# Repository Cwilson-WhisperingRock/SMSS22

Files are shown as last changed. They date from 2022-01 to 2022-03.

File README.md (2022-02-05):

SMSS22 : Smart Motor Syringe System
Winter 2022
Connor Wilson 

This repository is the lastest installment for the Smart Motor Syringe System.

~ Hub.py is the Hub controller file (raspberry Pi) that controls the three arduino motor controllers
	- The arduino motor controllers use Motor_controller.ino
		> Motor_controller.ino can be toggled to operate with the Hub.py using the #define I2C_COMMS
			or serial comms through the arduino IDE #define SERIAL_comms
			
~ Curses_Practice is a folder for getting familiar with the curses terminal GUI 

~ I2C_Practice is a folder for becoming familiar with I2C comms between the raspberry Pi's SMBus and arduino Wire libraries

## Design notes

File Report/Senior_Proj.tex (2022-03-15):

\documentclass[journal]{IEEEtran}
%
% If IEEEtran.cls has not been installed into the LaTeX system files,
% manually specify the path to it like:
% \documentclass[journal]{../sty/IEEEtran}

% *** CITATION PACKAGES ***
%
\usepackage[sorting =none]{biblatex}
\addbibresource{Citations.bib}

\usepackage{caption}
\usepackage{makecell}
\usepackage{fourier}
\usepackage{float}
\usepackage{color,soul}    
\usepackage{amssymb}

\usepackage{listings}
\usepackage{xcolor}

%New colors defined below
\definecolor{codegreen}{rgb}{0,0.6,0}
\definecolor{codegray}{rgb}{0.5,0.5,0.5}
\definecolor{codepurple}{rgb}{0.58,0,0.82}
\definecolor{backcolour}{rgb}{0.95,0.95,0.92}
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
  % declare the path(s) where your graphic files are
  % \graphicspath{{../pdf/}{../jpeg/}}
  % and their extensions so you won't have to specify these with
  % every instance of \includegraphics
  % \DeclareGraphicsExtensions{.pdf,.jpeg,.png}
\else
  % or other class option (dvipsone, dvipdf, if not using dvips). graphicx
  % will default to the driver specified in the system graphics.cfg if no
  % driver is specified.
  % \usepackage[dvips]{graphicx}
  % declare the path(s) where your graphic files are
  % \graphicspath{{../eps/}}
  % and their extensions so you won't have to specify these with
  % every instance of \includegraphics
  % \DeclareGraphicsExtensions{.eps}
\fi
% graphicx was written by David Carlisle and Sebastian Rahtz. It is
% required if you want graphics, photos, etc. graphicx.sty is already
% installed on most LaTeX systems. The latest version and documentation
% can be obtained at: 
% http://www.ctan.org/pkg/graphicx
% Another good source of documentation is "Using Imported Graphics in
% LaTeX2e" by Keith Reckdahl which can be found at:
% http://www.ctan.org/pkg/epslatex
%
% latex, and pdflatex in dvi mode, support graphics in encapsulated
% postscript (.eps) format. pdflatex in pdf mode supports graphics
% in .pdf, .jpeg, .png and .mps (metapost) formats. Users should ensure
% that all non-photo figures use a vector format (.eps, .pdf, .mps) and
% not a bitmapped formats (.jpeg, .png). The IEEE frowns on bitmapped formats
% which can result in "jaggedy"/blurry rendering of lines and letters as
% well as large increases in file sizes.
%
% You can find documentation about the pdfTeX application at:
% http://www.tug.org/applications/pdftex

% *** MATH PACKAGES ***
%
\usepackage{amsmath}
% A popular package from the American Mathematical Society that provides
% many useful and powerful commands for dealing with mathematics.
%
% Note that the amsmath package sets \interdisplaylinepenalty to 10000
% thus preventing page breaks from occurring within multiline equations. Use:
\interdisplaylinepenalty=2500
% after loading amsmath to restore such page breaks as IEEEtran.cls normally
% does. amsmath.sty is already installed on most LaTeX systems. The latest
% version and documentation can be obtained at:
% http://www.ctan.org/pkg/amsmath

% *** SPECIALIZED LIST PACKAGES ***
%
\usepackage{algorithmic}
% algorithmic.sty was written by Peter Williams and Rogerio Brito.
% This package provides an algorithmic environment fo describing algorithms.
% You can use the algorithmic environment in-text or within a figure
% environment to provide for a floating algorithm. Do NOT use the algorithm
% floating environment provided by algorithm.sty (by the same authors) or
% algorithm2e.sty (by Christophe Fiorio) as the IEEE does not use dedicated
% algorithm float types and packages that provide these will not provide
% correct IEEE style captions. The latest version and documentation of
% algorithmic.sty can be obtained at:
% http://www.ctan.org/pkg/algorithms
% Also of interest may be the (relatively newer and more customizable)
% algorithmicx.sty package by Szasz Janos:
% http://www.ctan.org/pkg/algorithmicx

% *** ALIGNMENT PACKAGES ***
%
\usepackage{array}
% Frank Mittelbach's and David Carlisle's array.sty patches and improves
% the standard LaTeX2e array and tabular environments to provide better
% appearance and additional user controls. As the default LaTeX2e table
% generation code is lacking to the point of almost being broken with
% respect to the quality of the end results, all users are strongly
% advised to use an enhanced (at the very least that provided by array.sty)
% set of table tools. array.sty is already installed on most systems. The
% latest version and documentation can be obtained at:
% http://www.ctan.org/pkg/array

% IEEEtran contains the IEEEeqnarray family of commands that can be used to
% generate multiline equations as well as matrices, tables, etc., of high
% quality.

\begin{document}
\graphicspath{ {./Images/} }
%
% paper title
% Titles are generally capitalized except for words such as a, an, and, as,
% at, but, by, for, in, nor, of, on, or, the, to and up, which are usually
% not capitalized unless they are the first or last word of the title.
% Linebreaks \\ can be used within to get better formatting as desired.
% Do not put math or special symbols in the title.
\title{Smart Motor Syringe System}
%
%
% author names and IEEE memberships
% note positions of commas and nonbreaking spaces ( ~ ) LaTeX will not break
% a structure at a ~ so this keeps an author's name from being broken across
% two lines.
% use \thanks{} to gain access to the first footnote area
% a separate \thanks must be used for each paragraph as LaTeX2e's \thanks
% was not built to handle multiple paragraphs
%

\author{Connor~Wilson,~\IEEEmembership{Member,~IEEE,} \\
        \small{EE Dept. Senior Project, \emph{California Polytechnic San Luis Obispo}, Winter 2022\\
        Advisor: Dr. Benjamin G. Hawkins}
        %John~Doe,~\IEEEmembership{Fellow,~OSA,}
        %and~Jane~Doe,~\IEEEmembership{Life~Fellow,~IEEE}% <-this % stops a space
%\thanks{B. Hawkins was with the Department
%of Electrical and Biomedical Engineering, California Polytechnic San Luis Obispo,
%CA, 93405 }% <-this % stops a space
%\thanks{Conrad Chan is with California Polytechnic San Luis Obispo}% <-this % stops a space
%\thanks{Manuscript received April 19, 2005; revised August 26, 2015.}}
}

% note the % following the last \IEEEmembership and also \thanks - 
% these prevent an unwanted space from occurring between the last author name
% and the end of the author line. i.e., if you had this:
% 
% \author{....lastname \thanks{...} \thanks{...} }
%                     ^------------^------------^----Do not want these spaces!
%
% a space would be appended to the last name and could cause every name on that
% line to be shifted left slightly. This is one of those "LaTeX things". For
% instance, "\textbf{A} \textbf{B}" will typeset as "A B" not "AB". To get
% "AB" then you have to do: "\textbf{A}\textbf{B}"
% \thanks is no different in this regard, so shield the last } of each \thanks
% that ends a line with a % and do not let a space in before the next \thanks.
% Spaces after \IEEEmembership other than the last one are OK (and needed) as
% you are supposed to have spaces between the names. For what it is worth,
% this is a minor point as most people would not even notice if the said evil
% space somehow managed to creep in.

% The paper headers
%\markboth{Journal of \LaTeX\ Class Files,~Vol.~14, No.~8, August~2015}%
%{Shell \MakeLowercase{\textit{et al.}}: Bare Demo of IEEEtran.cls for IEEE Journals}
% The only time the second header will appear is for the odd numbered pages
% after the title page when using the twoside option.
% 
% *** Note that you probably will NOT want to include the author's ***
% *** name in the headers of peer review papers.                   ***
% You can use \ifCLASSOPTIONpeerreview for conditional compilation here if
% you desire.

% If you want to put a publisher's ID mark on the page you can do it like
% this:
%\IEEEpubid{0000--0000/00\$00.00~\copyright~2015 IEEE}
% Remember, if you use this you must call \IEEEpubidadjcol in the second
% column for its text to clear the IEEEpubid mark.

% use for special paper notices
%\IEEEspecialpapernotice{(Invited Paper)}

% make the title area
\maketitle

% As a general rule, do not put math, special symbols or citations
% in the abstract or keywords.
\begin{abstract}
In this document a proof-of-concept design is developed and implementation to showcase the latest development in an ongoing effort to produce a series of automated syringe pumps.
\end{abstract}

% Note that keywords are not normally used for peerreview papers.
%\begin{IEEEkeywords}
%IEEE, IEEEtran, journal, \LaTeX, paper, template.
%\end{IEEEkeywords}

% For peer review papers, you can put extra information on the cover
% page as needed:
% \ifCLASSOPTIONpeerreview
% \begin{center} \bfseries EDICS Category: 3-BBND \end{center}
% \fi
%
% For peerreview papers, this IEEEtran command inserts a page break and
% creates the second title. It will be ignored for other modes.
\IEEEpeerreviewmaketitle

\section{Introduction}
    \IEEEPARstart{T}{here} is a desire to control flow rates in syringes in a steady and automated manner in the medical field; whether that be IV fluids or micro-fluids. According to PR NewsWire, the automated syringe pump market is currently valued at \$4 billion USD and is set to double its growth by 2030 \cite{cision}. These numbers suggest administering fluids in a controlled manner is a profitable and valuable piece of technology.
    
    However, this task is difficult to do manually, requiring precise digital control to achieve success. Because this device is related to medical and bio-engineering research, greater emphasis is placed on maintaining consistent flow rates and precision control. To achieve this key feature, typical syringe pumps utilize the precision of micro-controllers, large stepper motors, and reduction gear ratios in the drive train.
    
    With the introduction of precision control, keeping this project low cost is a secondary goal to make medical grade technology readily available. While existing products in the market are numerous, they are traditionally priced above \$1000 USD and are not easily programmable nor user friendly. Using readily available, non-proprietary hardware and software, I aim to provide reliable automated syringe systems for a fraction of the cost. This system of syringe pumps will also be controlled from a single controller, allowing the user to operate without manually addressing individual devices. This hub controller will add hierarchy that provides a more native and intuitive interface for the user, saving time and other resources used during setup.
    
    %Not sure if I should leave this part in or not??!
    It should be noted that my contribution to this project does not constitute a finished product but rather an ongoing pursuit for the minimum viable product as defined by Doctor Ben Hawkins.

\section{Background}

    \subsection{Purpose of a Syringe Pump}
        A syringe pump (or driver) is defined as a “small infusion pump, used to gradually
        administer small amounts of fluid (with or without medication) to a patient or for use in chemical and biomedical research.” \cite{wiki-pump} The need for slow incorporation of fluids is used in many applications. Intravenous (IV) therapies, for example, require syringe pumps in order to deliver medication over the course of several minutes or hours. Automating these doses removes most human error in high-risk procedures while saving the medical staff man-hours.
        
        \begin{figure}[H]
            \centering
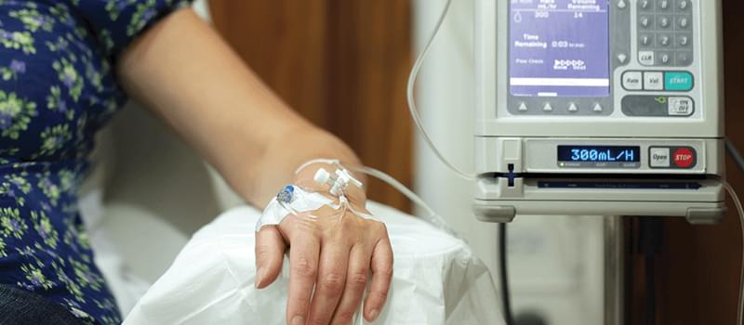
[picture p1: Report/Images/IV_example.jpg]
            
            \caption{Example of a Syringe Pump's IV Application \cite{howto-syringe}}
            \label{fig:IV_example}
        \end{figure}
        
        Additional uses for syringe pumps lie in micro-fluid research applications such as: enzyme kinetics, chemical synthesis, and potentially dangerous chemical reactions. For this project, the immediate use of this product will be for Dr. Ben Hawkins's research in enzyme solution gradients.
        
        \begin{figure}[H]
            \centering
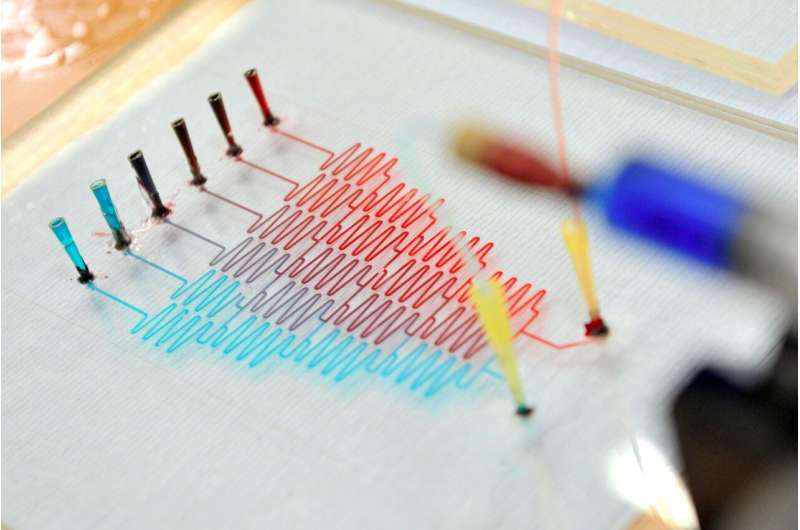
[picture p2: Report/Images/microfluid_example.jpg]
            
            \caption{Example of Microfluid Application \cite{mf_ex}}
            \label{fig:mf_example}
        \end{figure}
        
    \subsection{Description of the Smart Motor Syringe Pump}
    
        The SMSS (Smart Motor Syringe Pump) performs as the defined syringe pump, including but not limited to: output accurate/precise flow rates, display input/output hardware parameters, and control several syringe pumps, all while remaining under \$500 USD.
        
        The SMSS also aims to solve two problems, the first being inconsistent flow rates. Looking at existing technology, most low end pumps work on the basis of summing impulses over time such as the NE-300 in Figure \ref{fig:baddata_example}. An ideal pump would have smooth flow and quick transient responses. However, the main concern for the SMSS in this stage is to maintain a smooth flow rate and address sluggish response times in another prototype. Quintessentially, the SMSS is built to output flow rates that are precise and accurate. An understanding of the system’s plant and controller interface is required to operate within the desired tolerances and well worth the time investment. This will be discussed later in the paper.
        
         \begin{figure}[H]
            \centering
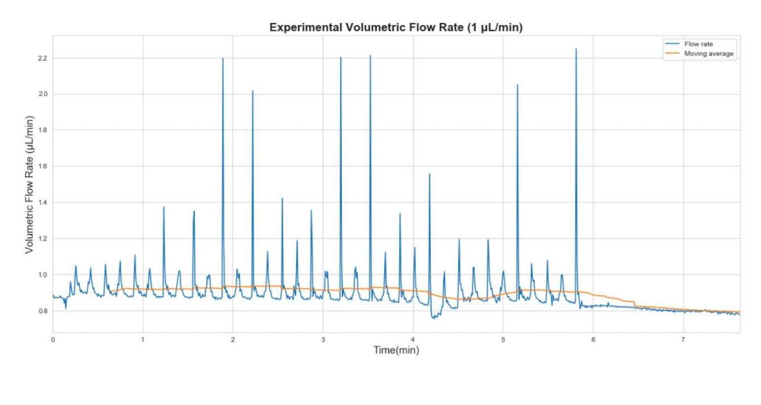
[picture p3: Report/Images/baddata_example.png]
            
            \caption{Output Flow from a NE-300 Syringe Pump \cite{conrads}}
            \label{fig:baddata_example}
        \end{figure}
        
        The second problem arises with the addition of other syringe pumps: multiple pumps will often require a synchronized start/stop time from which to collect data from. The main/sub hierarchy implemented aims to synchronize the start/stop of several units and eliminate the errors presented when triggering each pump manually. 
        
        Looking broadly at this project, the SMSS aligns with a research market: laboratory applications that deliver small amounts of fluid while collecting data on the system. It should be noted that while syringe pumps can differ in applications, their internal structure is the same: they all consist of a stepper motor, pusher block, and a syringe holder (Figure \ref{fig:Pump_example}). 
        
        \begin{figure}[H]
            \centering
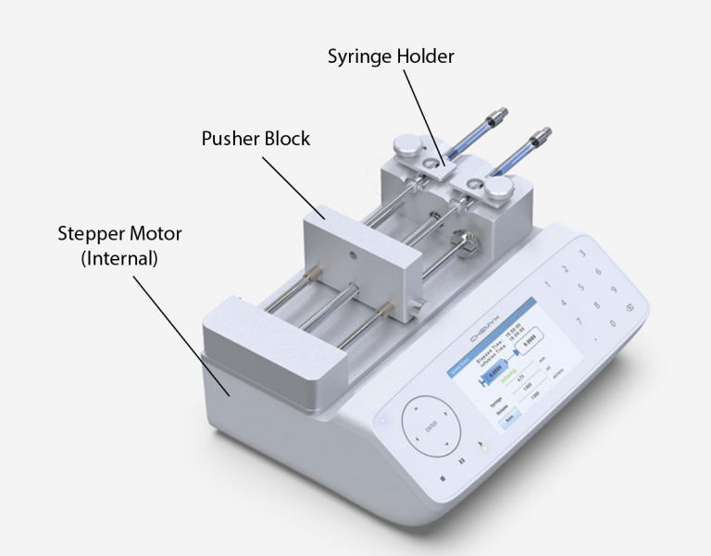
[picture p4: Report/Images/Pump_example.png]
            
            \caption{Components of a Syringe Pump \cite{example-syringe}}
            \label{fig:Pump_example}
        \end{figure}

        The SMSS makes use of the Raspberry Pi 3's computing power by implementing a display for the user; a feature forgotten on some devices on the market. The user interface prompts for user requests but also informs the user of resulting error codes, run time, and hardware issues with their requests.

\section{Product Planning and Research} 
    Evaluation of the SMSS and it's viability as a product requires an analysis of existing technology on the market. Only when I looked at the existing products could I determine the engineering requirements and priority of each.
    
    \subsection{Marketing}
        This subsection is focused on the marketing aspect of a syringe pump in an attempt to translate customer needs into a viable and cost effective product.
        
        \subsubsection{Marketing Research}
            Using Google's tool for search trends, there was a low number of searches in the US and internationally for syringe pumps. This signals that the amount of new customers looking to purchase an SMSS is small, or that existing customers in the market do not use Google to search for new products. These customers might look to a medical supplier or academic group when looking for a new syringe pump. The Dublin PRNewswire \cite{cision} has stated that the IV pump market is valued at \$4 billion USD (in 2020) and is expected to double by 2030. This speculation is pre-COVID but it does hold some merit. Looking at Figure \ref{fig:intern_interest}, there appears to be a larger customer base outside the US; range for Figure \ref{fig:intern_interest} is $\in$ (12-211) hits in January 2021.
            
            \begin{figure}[H]
                \centering
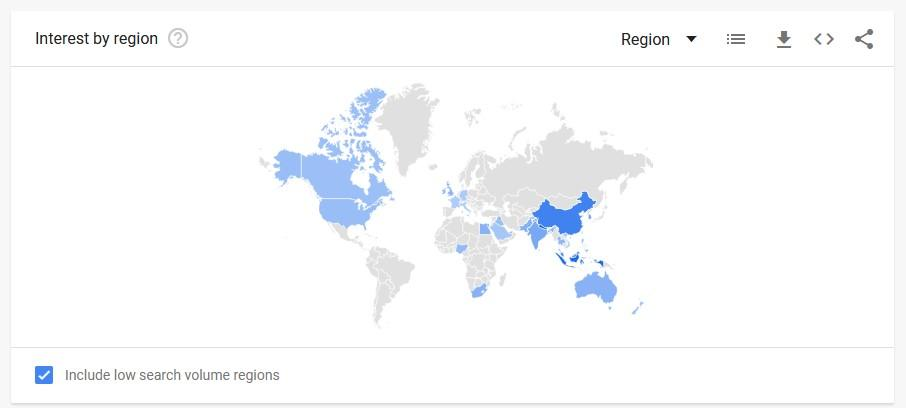
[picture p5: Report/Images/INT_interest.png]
                
                \caption{Global Google Search of "Syringe Pump" 2021 \cite{goog_trend}}
                \label{fig:intern_interest}
            \end{figure}
        
            Further information was gathered in Figure \ref{fig:search_option} when searching for syringe pumps: there are many applications and characteristics for existing products on the market. My sole customer's [Dr. Hawkins] request for a research-oriented device represents smaller portion when compared to infusions, but it should be noted that the SMSS can achieve the minimum viable product for multiple applications. Qualifying for various FDA medical device classes will be left up to the next iteration of the SMSS.
            
            \begin{figure}[H]
                \centering
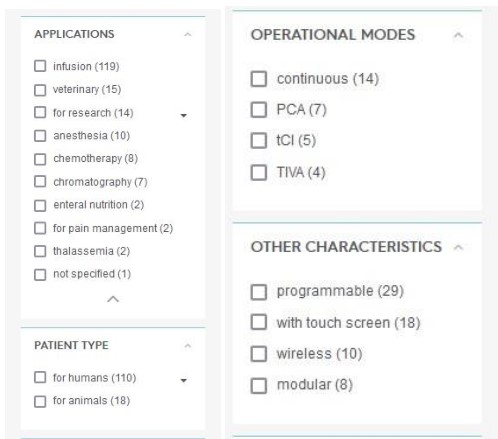
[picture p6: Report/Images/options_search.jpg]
                
                \caption{Options for Pumps in MedicalExpo.com \cite{goog_device}}
                \label{fig:search_option}
            \end{figure}

        \subsubsection{Customer Archetype}
            The Smart Motor Syringe System has many established competitors in the market but none have a portion over 40\%. All of these competitors have costly devices nearing \$5000 USD but come with features such as failure alarms, custom fluid capacity syringes, unique flow patterns, and battery backup power. However, after viewing a handful of device data sheets on MedicalExpo.com \cite{goog_device}, very few competitors provide testing data or flow rate tolerances. With our main customer being research oriented, the sensitivity of the pump's output is important. I believe bolstering and advertising the engineering requirements on top of the SMSS's steady output as the minimum viable product will carve out a spot in the syringe pump market.
            
            The table below provides three examples of the customer base.
            
            \begin{table}[H]
                \renewcommand{\arraystretch}{1.3}
                \caption{Customer Archetype}
                \label{table:CustArch}
                \begin{center}
                    \begin{tabular}{|c|c|c|c|}
                        \hline
                        \bfseries Customer&
                        \bfseries Description&
                        \bfseries Reason&
                        \bfseries Product Use\\
                        \hline
                        
                        \makecell[l]{Research\\Student}&
                        \makecell[l]{This group is \\
                                     likely to ad-\\
                                     opt new tech-\\
                                     nologies with\\
                                     an emphasis on\\
                                     easy-use DIY\\
                                     and low cost.}&
                        \makecell[l]{This group aims\\
                                     to utilize the\\
                                     minimum viable\\
                                     product aspect\\
                                     while remain-\\
                                     ing open to \\
                                     learning exper-\\
                                     iences around\\
                                     DIY and emerg-\\
                                     ing tech. The\\
                                     ability to buy\\ 
                                     multiple units\\
                                     and sync them\\
                                     is important\\
                                     for testing \\
                                     data.}&
                        \makecell[l]{This group will\\
                                     utilize this pr-\\
                                     oduct frequently\\
                                     but not in a \\
                                     commercial set-\\
                                     ting. I can exp-\\
                                     ect his product\\
                                     to remain rele-\\
                                     vant for a long\\
                                     period until re-\\
                                     placement over\\
                                     the course of \\
                                     a decade.}\\
                        \hline
                        
                        \makecell[l]{Remote\\Medical\\Worker}&
                        \makecell[l]{These customers\\
                                     are looking for\\
                                     a robust solut-\\
                                     ion that can be\\
                                     torn open and \\
                                     repaired. Cost\\
                                     is likely to be\\
                                     a factor.}&
                        \makecell[l]{Practicing medi-\\
                                     cine in remote\\
                                     locations means\\
                                     that supplies \\
                                     are limited. The\\
                                     need for medical\\
                                     attention will\\
                                     still require med-\\
                                     ical equipment.}&
                        \makecell[l]{This group will\\
                                     likely run the\\
                                     equipment into\\
                                     the ground and\\
                                     replace parts \\
                                     themselves. Cost\\
                                     is a strong fact-\\
                                     or as well as \\
                                     robustness and\\
                                     open-source \\
                                     likeness}\\
                        \hline
                        
                        \makecell[l]{Third-\\World\\Medical\\Center}&
                        \makecell[l]{These customers\\
                                     care most about\\
                                     the cost of the\\
                                     product as well\\
                                     as the function-\\
                                     ality. MVP and \\
                                     functionality \\
                                     are critical}&
                        \makecell[l]{Currency may \\
                                     not be equal \\
                                     to USD and req-\\
                                     uire a large \\
                                     portion of the\\
                                     budget to buy \\
                                     basic medical \\
                                     equipment.}&
                        \makecell[l]{[Same as above]}\\
                        \hline
        
                    \end{tabular}
                \end{center}
            \end{table}
            
            The following table outlines competitors in the market. It should be noted that most companies are overseas and have a large pool of products related to the medical field. This list is not shy of catheters, IV fluids, syringes, thermal components, 3-D imaging machines, and other augmented devices. One example is Norgren, a large Switzerland company. They have an international presence here in the US that shouldn't be excluded when researching domestic markets in the US. I should mention that it is not easy to track companies as a whole entity, but rather its branches and partners. Wellead is an example of a company here in the US that is difficult to contact or buy from locally. I believe a portion of these companies have third parties to sell and establish their branding within the medical market.
            
            The table below provides four examples of competing companies.
            
            \begin{table}[H]
                \renewcommand{\arraystretch}{1.3}
                \caption{Market Competitors}
                \label{table:Mark_compet}
                \begin{center}
                    \begin{tabular}{|c|c|}
                        \hline
                        \bfseries Market Leader&
                        \bfseries Description\\
                        \hline

                        
                        \cite{goog_device}&
                        \makecell[l]{Specializes in\\
                                     veterinary medical\\
                                     devices (Located\\
                                     in China)}\\
                        \hline
                        
                        
                        \cite{goog_device}&
                        \makecell[l]{Specialized in\\
                                     a wide variety \\
                                     of syringe pumps\\
                                     and medical equip-\\
                                     ment. One of the \\
                                     top 10 medical \\
                                     companies in this\\
                                     field. (Located in\\
                                     USA)}\\
                        \hline
                        
                        
                        \cite{goog_device}&
                        \makecell[l]{A small company \\
                                     with a good prod-\\
                                     uct line. (Located\\
                                     in China)}\\
                        \hline
                        
                        
                        \cite{goog_device}&
                        \makecell[l]{A pipetting comp-\\
                                     any that makes \\
                                     channel pumps and\\
                                     syringe pumps. \\
                                     (Located in Swit-\\
                                     zerland)}\\
                        \hline

                    \end{tabular}
                \end{center}
            \end{table}
            
        \subsubsection{Marketing Requirements}
            The SMSS's marketing requirements are derived from the business model and marketing data model in Appendix \ref{Appendix:Documents} Figure \ref{fig:business_sheet}/\ref{fig:market_sheet} with Professor Ben Hawkins. In depth, Dr. Hawkins's technological needs are a large influence on the project. That being said, the SMSS stands to be a marketable product in the medical sector.
            
            \begin{table}[H]
                \renewcommand{\arraystretch}{1.3}
                \caption{Marketing Requirements}
                \label{table:MarketingReq}
                \begin{center}
                    \begin{tabular}{|c|c|c|}
                        \hline
                        \bfseries \# & \bfseries Marketing Requirement & \bfseries Justification \\
                        \hline
                        
                        1 & \makecell{High precision/accuracy \\ flow rates} &  \makecell[l]{Constitutes the use of auto-\\
                                     mation, to avoid human incon-\\
                                     sistencies and save labor.}\\
                        \hline
                        
                        2 & Programmable flow rates & 
                        \makecell[l]{Customers need various flow\\
                                     rates for different app-\\
                                     lications.} \\
                        \hline
                        
                        3 & Modular & 
                        \makecell[l]{Customer’s require multiple\\
                                     pumps to be controlled in a\\
                                     single project while being\\
                                     able to change setup and\\
                                     hierarchy.} \\
                        \hline
                        
                        4 & Affordable cost (Priced \$500)  & 
                        \makecell[l]{This cheaper price point\\
                                     appeals to budget-\\
                                     concerned customers} \\
                        \hline
                        
                        5 & Easy User Interface & 
                        \makecell[l]{Users should enjoy using\\
                                     the device.} \\
                        \hline
                        
                        6 & Reliable & 
                        \makecell[l]{Critical work depends\\
                                     on this device} \\
                        \hline
        
                    \end{tabular}
                \end{center}
            \end{table}
            
            The highest priority of the project is to produce high precision/accuracy flow rates from a standard syringe. The customer, Dr. Hawkins, requested that the pump perform to the same tolerance as existing products while avoiding impulse problems. This requirement does inadvertently imply the use of water in the syringe pumps: the viscosity of the fluid will change the flow rate and the accuracy of the device.
            
            The next highest priority is programmable flow rates: allowing the user to achieve a desired flow rate from the available hardware in a jog or timed manner. This requirement does also inadvertently imply that the only mechanical signal acting on the syringes are unit steps that only produce constant flow. Additional mechanical signals such as a ramp, triangle, or exponential function are not within the scope of this version of the SMSS.
            
            A modular marketing requirement states the user has ability to use a single pump or scale the project up to three pumps. In another frame, the SMSS function without a complete set of devices.
            
            An affordable price point is market disrupting while outperforming the competition with other higher priority qualities. An affordable cost also dictates a lower cost per iteration of the project; this student project will continue to build in complexity without inflating in cost.
            
            An easy interface is a key point as the user shouldn't be required to code or write scripts to use the device. A low learning curve for the device keeps the SMSS competitive and relevant with current Cal Poly research projects outside the electrical engineering department.
            
            Reliability is the last marketing requirement and it is last because the SMSS is still in a prototype state. Reliability for the SMSS is hardware robustness and resistance to various types of noise in the field. This could be interpreted in many ways: study housing, noise rejection, operating in partial failure modes, etc. 
        
    \subsection{Engineering Requirements}
        The engineering requirements seen in the table below are derived from the marketing requirements in Appendix \ref{Appendix:Documents} Table \ref{table:MarketingReq}. In order to meet the market requirements of the customer, these engineering requirements were tested and validated before release. This list is not all encompassing,nor in order of priority, but does outline the minimum viable product to remain competitive in the market. It should also be noted that the requirements derived here are set for this specific version of the SMSS and not guaranteed to hold between generations.
        
        Verification of these requirements covers a wide array of testing setups and is discussed in the Testing section of the paper. 
        
         \begin{table}[H]
            \renewcommand{\arraystretch}{1.3}
            \caption{Engineering Requirements}
            \label{table:EngineeringReq}
            \begin{center}
                \begin{tabular}{|c|c|c|}
                    \hline
                    \makecell{\bfseries Market\\ \bfseries Req.} & 
                    \makecell{\bfseries Engineering\\ \bfseries Req.} & 
                    \bfseries Justification \\
                    \hline
                    
                    4 & 
                    \makecell[l]{Total production shouldn't\\ 
                                 exceed \$500} &  
                    \makecell[l]{This covers cost (with net\\
                                 profit) while remaining\\
                                 competitive in the low-end\\
                                 market}\\
                    \hline
                    
                    1,6 &
                    \makecell[l]{The pump shall hold a mini\\
                                 -mum flow rate of 0.1$\frac{mL}{hr}$\\
                                 within $\pm$0.01$\frac{mL}{sec}$ of target\\
                                 rate.} & 
                    \makecell[l]{Similar products have this\\
                                 tolerance and the applica-\\
                                 tion of the pump needs to\\
                                 remain relevant for med-\\
                                 ical purposes} \\
                    \hline
                    
                    1,6 & 
                    \makecell[l]{The pump shall hold a max-\\
                                 imum flow rate of 100$\frac{mL}{hr}$\\
                                 within $\pm \, 0.01 \frac{mL}{sec}$ of target\\
                                 rate.} & 
                    \makecell[l]{Similar products have this\\
                                 tolerance and the applica-\\
                                 tion of the pump needs to\\
                                 remain relevant for med-\\
                                 ical purposes} \\
                    \hline
                    
                    4 & 
                    \makecell[l]{The pump shall not contain\\
                                 proprietary software or \\
                                 hardware.} &
                    \makecell[l]{I want to avoid costly parts\\
                                 that could be difficult to\\
                                 alter.} \\
                    \hline
                    
                    3 & 
                    \makecell[l]{The pump must be able to \\
                                 house syringes of size 2mL\\
                                 to 20mL} &
                    \makecell[l]{Dynamic range of syringes\\
                                 is necessary for compati-\\
                                 bility of products in the\\
                                 field.} \\
                    \hline
                    
                    2,3 & 
                    \makecell[l]{The hub controller must\\
                                 be able to handle 3 pum-\\
                                 ps with same flow rates.} & 
                    \makecell[l]{Scaling to 3 pumps is de-\\
                                 fined by the customer} \\
                    \hline
                    
                     5 & 
                    \makecell[l]{The controller shall have\\
                                 a GUI.} &  
                    \makecell[l]{The product needs to be \\
                                 useful for a wide audience} \\
                    \hline
                    
                    3,4 & 
                    \makecell[l]{The drive train and hous-\\
                                 ing of the pump can be \\
                                 3D printed.} &  
                    \makecell[l]{The product should remain\\
                                 available to a wide range\\
                                 of personnel and institu-\\
                                 tions.} \\
                    \hline
                    
                    1,2,5 & 
                    \makecell[l]{The controller must be \\
                                 able to output digital \\
                                 log information on out-\\
                                 put flow rates: 255 Sam-\\
                                 ples $\in$ (1min, 30min, 1hr\\
                                 6hr, 24hrs, 2days, 1wk)} &  
                    \makecell[l]{The product needs to be \\
                                 able to provide resear-\\
                                 chers with data they can\\
                                 analyze.} \\
                    \hline

                \end{tabular}
            \end{center}
        \end{table}
        
    \subsection{Scheduling}
        The current GANNT chart on the SMSS is seen in Appendix \ref{Appendix:Documents} Figure \ref{fig:Gantt}. This GANTT was utilized to the best of its predictions but was not a living document for the duration of the quarter. 

    \subsection{Bill of Materials}
        The SMSS project ideally requires funding for parts and labor. The chart in Appendix \ref{Appendix:Documents} Figure \ref{fig:BoM} outlines the current status of the market pricing as of March 2022 and the stockroom of this continuous project. Furthermore, my contribution to this project is highlighted in orange and added to the overall cost of the project. The total funding required for the system is below \$500 USD with some items missing documentation from previous work.

        Additional man hours have been added for adequate time to debug and perform software validations. It was increased from 20 hours a week to 45 given the condensed time frame and large portions of software. 

\section{System Design}
    The Smart Motor Syringe System is a mixture of both hardware and software. The following section discusses both aspects of the device in detail.
    
    \subsection{System Hierarchy}
        The SMSS has many layers to its complexity. For the sake of clarity, a functional decomposition is illustrated below.
        
        \subsubsection{Functional Decomposition (Level 0) }
            In the highest level of the SMSS, the black box diagram of the system is comprised of three inputs and three outputs. The inputs of the device are: 120VAC from a power outlet, a single or series of syringes, and user requests from the GUI. The outputs are: linear force placed on the plunger of the syringe, a GUI display for the user, and output flow rate data. 
            
            The user will load a syringe into the device, supply power and interact with the GUI by enter the requested data from the SMSS on a keyboard. The requested data for each pump includes the volumetric flow rate, radius of the syringe, capacity of the syringe, and the duration of the device. Upon starting, the device will run the motors and supply enough linear force to produce the requested flow rate. Depending on the user selection, a stop can be time sensitive or triggered manually. 
            
            \begin{figure}[H]
                \centering
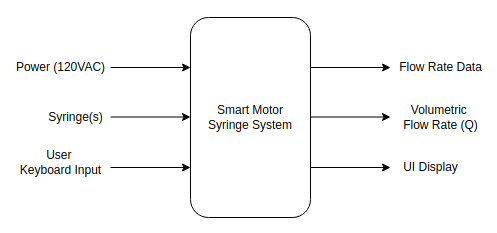
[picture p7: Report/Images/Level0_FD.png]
                
                \caption{Level 0 of the SMSS}
                \label{fig:level0}
            \end{figure}

            \begin{table}[H]
            \renewcommand{\arraystretch}{1.3}
            \caption{Design Level 0}
            \label{table:Level0}
                \begin{center}
                    \begin{tabular}{|c|c|}
                        \hline
                        \bfseries Market &
                        \bfseries SMSS\\
                        \hline
                        
                        Inputs & 
                        \makecell[l]{
                            \(\bullet\) Power, 120 VAC\\ 
                            \(\bullet\) Syringe \(\in\) [1mL, 30mL] \\
                            \(\bullet\) User input from keyboard\\
                        }\\
                        \hline 
                        
                        Outputs & 
                        \makecell[l]{
                            \(\bullet\) Volumetric flow rate (Q) from syringe \\
                            \(\bullet\) Flow rate data \\
                            \(\bullet\) User interface display
                        }\\
                        \hline
                        
                        Functionality & 
                        \makecell[l]{
                            After supplying power and water-filled \\
                            syringe(s), the user will interact with\\
                            the GUI and enter hardware metrics (on \\
                            a keyboard) for each pump. After starting\\
                            the machine, it will produce linear force\\
                            on each syringe along with measured flow\\
                            rate data from each device. The GUI will\\
                            visually displayed for the user on a monitor.
                        }\\
                        \hline

                    \end{tabular}
                \end{center}
            \end{table}
        
        \subsubsection{Functional Decomposition (Level 1) }
            The next level of hierarchy, Figure \ref{fig:level1}, further breaks down the system into individual sections. The motor power supply (VMOT), digital power (VDIG), and syringes are split respectively for simplicity. The hub controller is a GUI driven controller designed to send commands to each of the pump controllers. It is separated from the other pump controllers to highlight its higher hierarchical place as well as it's interaction with user inputs/output devices. It also acts as a main device with the pump controllers assuming the sub role for I2C communication protocol; the hub controller also supplies VDIG to all of the individual pump controllers. Lastly, the pump controllers are the electrical and mechanical hardware used to translate electrical quantities into linear force. This is a large set of equipment that demands an additional level of decomposition to break down cleanly; this is seen in Figure \ref{fig:level2}.
            
            \begin{figure}[H]
                \centering
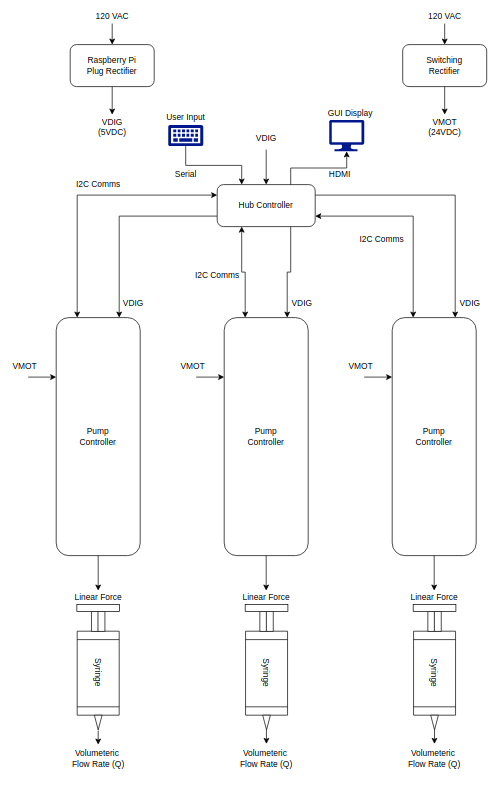
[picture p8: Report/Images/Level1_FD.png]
                
                \caption{Level 1 of the SMSS}
                \label{fig:level1}
            \end{figure}
        
            \begin{table}[H]
            \renewcommand{\arraystretch}{1.3}
            \caption{Switching Power Supply in Level 1}
            \label{table:switching_power_1}
                \begin{center}
                    \begin{tabular}{|c|c|}
                        \hline
                        \bfseries Module & Switching Rectifier \\ \hline
                        \bfseries Input & \makecell[l]{120 VAC} \\ \hline
                        \bfseries Output & \makecell[l]{24VDC (VMOT)} \\ \hline
                        \bfseries Function & 
                            \makecell[l]{Convert the 120 VAC wall source \\
                                         and provide the stepper motors \\
                                         with 24VDC and +1A continuous \\
                                         current.}  \\ \hline
                    \end{tabular}
                \end{center}
            \end{table}

            \begin{table}[H]
            \renewcommand{\arraystretch}{1.3}
            \caption{Digital Power Supply in Level 1}
            \label{table:ditigal_power_1}
                \begin{center}
                    \begin{tabular}{|c|c|}
                        \hline
                        \bfseries Module & Plug Rectifier \\ \hline
                        \bfseries Input & \makecell[l]{120 VAC} \\ \hline
                        \bfseries Output & \makecell[l]{5 VDC (VDIG)} \\ \hline
                        \bfseries Function & 
                            \makecell[l]{Convert the 120 VAC wall source \\
                                         and provide the Raspberry Pi \\
                                         with 5VDC and +1A continuous \\
                                         current.} \\ \hline
                    \end{tabular}
                \end{center}
            \end{table}

            \begin{table}[H]
            \renewcommand{\arraystretch}{1.3}
            \caption{GUI Display in Level 1}
            \label{table:display_1}
                \begin{center}
                    \begin{tabular}{|c|c|}
                        \hline
                        \bfseries Module & Display Monitor \\ \hline
                        \bfseries Input & \makecell[l]{HDMI from hub controller} \\ \hline
                        \bfseries Output & \makecell[l]{Visual information for user} \\ \hline
                        \bfseries Function & \makecell[l]{The monitor displays the GUI for the user} \\ \hline
                    \end{tabular}
                \end{center}
            \end{table}

            \begin{table}[H]
            \renewcommand{\arraystretch}{1.3}
            \caption{User Input in Level 1}
            \label{table:keyboard_1}
                \begin{center}
                    \begin{tabular}{|c|c|}
                        \hline
                        \bfseries Module & Keyboard \\ \hline
                        \bfseries Input & \makecell[l]{User key press} \\ \hline
                        \bfseries Output & \makecell[l]{Serial signal for controller} \\ \hline
                        \bfseries Function & \makecell[l]{Translates user key presses into digital signals} \\ \hline
                    \end{tabular}
                \end{center}
            \end{table}

            \begin{table}[H]
            \renewcommand{\arraystretch}{1.3}
            \caption{Hub Controller in Level 1}
            \label{table:Hub_1}
                \begin{center}
                    \begin{tabular}{|c|c|}
                        \hline
                        \bfseries Module & Hub Controller \\ \hline
                        \bfseries Input & 
                            \makecell[l]{\(\bullet\)5 VDC\\
                                         \(\bullet\)User data from Keyboard\\
                                         \(\bullet\)I2C response from motor controller\\
                                         \(\bullet\)Measured flow rate data from motor controller\\ }\\ \hline
                        \bfseries Output &
                            \makecell[l]{\(\bullet\)5 VDC\\
                                         \(\bullet\)GUI display on monitor\\
                                         \(\bullet\)I2C commands for motor controller\\
                                         \(\bullet\)Compiled flow rate data from each pump \\}\\ \hline
                        \bfseries Function & 
                            \makecell[l]{Directs the state of each motor controller \\unit,              translates user requests into usable data, \\
                                         and stores measured flow rate data from each\\
                                         unit.}\\ \hline
                    \end{tabular}
                \end{center}
            \end{table}

            \begin{table}[H]
            \renewcommand{\arraystretch}{1.3}
            \caption{Syringe in Level 1}
            \label{table:syringe_1}
                \begin{center}
                    \begin{tabular}{|c|c|}
                        \hline
                        \bfseries Module & Syringe \\ \hline
                        \bfseries Input &  \makecell[l]{\(\bullet\)Linear force\\
                                                        \(\bullet\)Water\\} \\ \hline
                        \bfseries Output & \makecell[l]{Volumetric Flow (Q)} \\ \hline
                        \bfseries Function & Translates linear force into flow rate \\ \hline
                    \end{tabular}
                \end{center}
            \end{table}
            
            \begin{table}[H]
            \renewcommand{\arraystretch}{1.3}
            \caption{Pump Controller in Level 1}
            \label{table:controller_level1}
                \begin{center}
                    \begin{tabular}{|c|c|}
                        \hline
                        \bfseries Module & Pump Controller \\ \hline
                        \bfseries Input & \makecell[l]{\(\bullet\)5 VDC (VDIG)\\
                                                       \(\bullet\)24VDC (VMOT)\\
                                                       \(\bullet\)I2C commands from Hub\\
                                                        }\\ \hline
                        \bfseries Output & \makecell[l]{\(\bullet\)Linear force on syringe\\
                                                       \(\bullet\)I2C response to Hub\\
                                                       \(\bullet\)Measured flow rate to               Hub\\}\\ \hline
                        \bfseries Function & \makecell[l]{The motor controller and plant system are\\
                                                          responsible for translating the hub comm-\\
                                                          ands into a linear force as well as supply\\
                                                          the hub with response information and flow\\        rate data. }\\ \hline
                    \end{tabular}
                \end{center}
            \end{table}
            
        \subsubsection{Functional Decomposition (Level 2)}
        
            Level 2 of the functional decomposition focuses on an individual pump controller and the electrical/mechanical components inside. The top block in Figure \ref{fig:level2} is the motor controller. For this version of the SMSS, the motor controller is an Arduino Nano that is connected to the hub controller with I2C and digital power VDIG. The motor controller controls the local logic flow and adjusts the setting/performance of the stepper motor (indirectly through the stepper driver). The stepper driver translates the low power signals from the motor controller into a high-power signal usable by the stepper motor. Lastly, the ball screw translates the rotation of the stepper motor into linear velocity.
            
            \begin{figure}[H]
                \centering
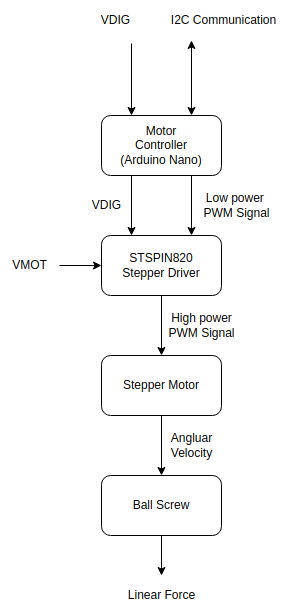
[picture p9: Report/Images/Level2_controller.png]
                
                \caption{Level 2 of the Pump Controller}
                \label{fig:level2}
            \end{figure}

            \begin{table}[H]
            \renewcommand{\arraystretch}{1.3}
            \caption{Motor Controller in Pump Controller Level 2}
            \label{table:motor_control_2}
                \begin{center}
                    \begin{tabular}{|c|c|}
                        \hline
                        \bfseries Module & Motor Controller \\ \hline
                        \bfseries Input & \makecell[l]{\(\bullet\)5 VDC (VDIG)\\
                                                       \(\bullet\)Bi-directional I2C communication\\
                                                       }\\ \hline
                        \bfseries Output & \makecell[l]{\(\bullet\)5 VDC (VDIG)\\
                                                       \(\bullet\)Low power PWM signal\\
                                                       }\\ \hline
                        \bfseries Function & \makecell[l]{The motor controller converts hub controller requests\\                                   into a PWM signal for the stepper driver. The \\
                                                          motor controller collects flow rate data and can act\\
                                                          as a standalone device should the user only need one\\ pump.}  \\ \hline
                    \end{tabular}
                \end{center}
            \end{table}
            
            \begin{table}[H]
            \renewcommand{\arraystretch}{1.3}
            \caption{Stepper Driver in Pump Controller Level 2}
            \label{table:stepper_control_2}
                \begin{center}
                    \begin{tabular}{|c|c|}
                        \hline
                        \bfseries Module & Stepper Driver \\ \hline
                        \bfseries Input & \makecell[l]{\(\bullet\)5 VDC (VDIG)\\
                                                       \(\bullet\)24 VDC (VMOT)\\  
                                                       \(\bullet\)5v logic level PWM signal\\
                                                       }\\ \hline
                        \bfseries Output & \makecell[l]{24v logic level PWM signal}\\ \hline
                        \bfseries Function & 
                            \makecell[l]{The stepper driver takes in a relatively low\\
                                         voltage PWM signal, modulates that signal with\\
                                         VMOT, and outputs a higher power PWM signal\\
                                         with options for step division (micro stepping).}\\ \hline
                        
                    \end{tabular}
                \end{center}
            \end{table}

            \begin{table}[H]
            \renewcommand{\arraystretch}{1.3}
            \caption{Stepper Motor in Pump Controller Level 2}
            \label{table:stepper_2}
                \begin{center}
                    \begin{tabular}{|c|c|}
                        \hline
                        \bfseries Module & Stepper Motor \\ \hline
                        \bfseries Input & \makecell[l]{High power PWM} \\ \hline
                        \bfseries Output & \makecell[l]{Angular velocity \(\omega\)} \\ \hline
                        \bfseries Function & 
                            \makecell[l]{Converts the PWM pulses into rotational movement.}  \\ \hline
                    \end{tabular}
                \end{center}
            \end{table}
            
            \begin{table}[H]
            \renewcommand{\arraystretch}{1.3}
            \caption{Ball Screw in Pump Controller Level 2}
            \label{table:ballscrew_2}
                \begin{center}
                    \begin{tabular}{|c|c|}
                        \hline
                        \bfseries Module & Ball Screw \\ \hline
                        \bfseries Input & \makecell[l]{Rotational Velocity} \\ \hline
                        \bfseries Output & \makecell[l]{Linear force (and velocity)} \\ \hline
                        \bfseries Function & 
                            \makecell[l]{Convert the rotation of the motor into linear\\
                                         force/velocity.}  \\ \hline
                    \end{tabular}
                \end{center}
            \end{table}

    \subsection{Hub Controller}
        This subsection discusses the hub controller, covering the GUI interface as well as the logic flow. The user interface will be a step-by-step example walk through that covers all of the interactions the user will come across. The logic flow will be presented with flow diagrams and outlines. 
        
        \subsubsection{User Interface}
            The user interface uses a terminal-based library called Curses or NCurses. This library is already installed on most OS and is usually seen in BIOS menus or other applications requiring a lightweight GUI. It should be noted that curses operates in the terminal, often forgoing the use of a mouse and relying solely on the keyboard for user input. Curses does offer mouse integration but due to  time constraints, the keyboard will be the only input device for the hub controller while in the terminal. It is still recommended to use a mouse to interact with the raspberry pi. 
            
            Upon powering the hub controller (or raspberry pi for this version of SMSS), a yellow LED will light up. This light is attached to the STANDBY state of the motor controller (Arduino Nano). Table \ref{table:LED_explain} pairs the corresponding color combination of LED to the motor controllers current state. 
        
            \begin{table}[H]
                \renewcommand{\arraystretch}{1.3}
                \caption{Device State per LED Combination}
                \label{table:LED_explain}
                    \begin{center}
                        \begin{tabular}{|c|c|}
                            \hline
                            \bfseries LED & \bfseries State \\ \hline
                            Yellow & \makecell[l]{Standby}  \\ \hline
                            Blue & \makecell[l]{Data collection ("Datapull") for timed run\\ mode.}\\ \hline
                            Blue + White & \makecell[l]{Data collection ("Datapull") for jog mode.}\\ \hline
                            Green & \makecell[l]{Motor running in timed run mode.} \\ \hline
                            Green + White & \makecell[l]{Motor running in jog mode.} \\ \hline
                        \end{tabular}
                    \end{center}
                \end{table}
            
            Figure \ref{fig:GUI0_L} shows the starting condition of three syringe pumps and their yellow STANDBY LEDs. The LEDs located on the three Nano boards do not represent the controller states; only the three rows of LEDs off of the boards are status LEDs. It should be noted that device one is the right-most device, progressing numerically to the left (the left-most device is number 3). 
            
            \begin{figure}[H]
                \centering
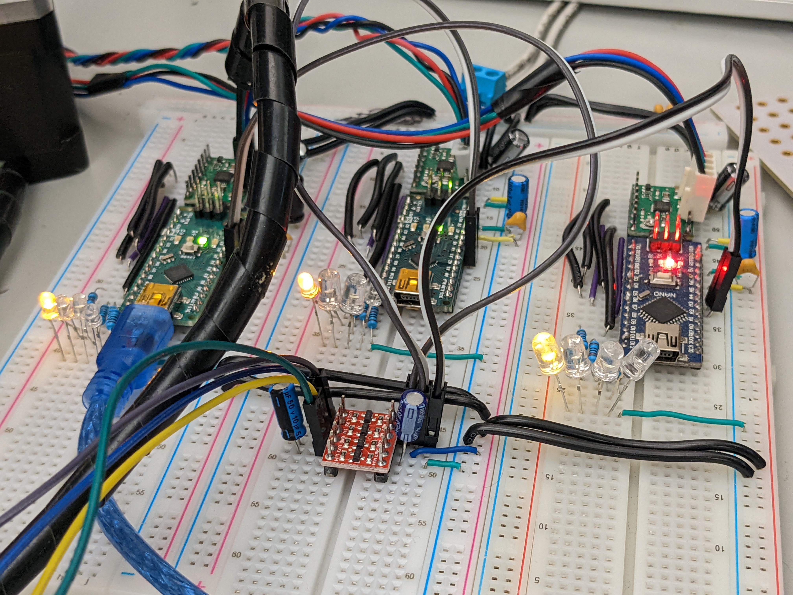
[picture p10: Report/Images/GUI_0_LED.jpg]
                
                \caption{LED Indicators on Start}
                \label{fig:GUI0_L}
            \end{figure}
            
            Figure \ref{fig:Term_hub} shows the command lines to navigate the user to the GUI. The first line, \emph{cd Desktop/SMSS22}, changes the terminal directory to the location of the hub controller's python file. the next line, \emph{python3 Hub.py} runs the python script. It is recommended to resize the terminal window to a larger one before pressing enter. 
            
            \hl{** The user can press CTRL+z to exit the GUI. **}
            
            \begin{figure}[H]
                \centering
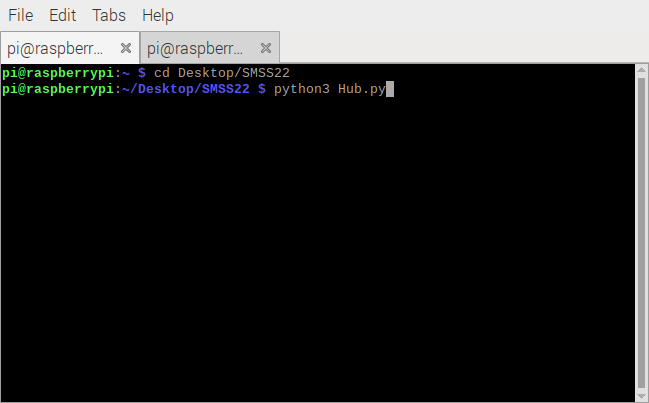
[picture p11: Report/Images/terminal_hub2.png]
                
                \caption{Running Hub.py in the Terminal}
                \label{fig:Term_hub}
            \end{figure}
            
            Figure \ref{fig:keys_states} represents the controls for selecting the device run states as well as the direction of the motors in a later menu. The WASD keys are used to move the highlighted cursor left/right with W acting as the enter key.
            
            \begin{figure}[H]
                \centering
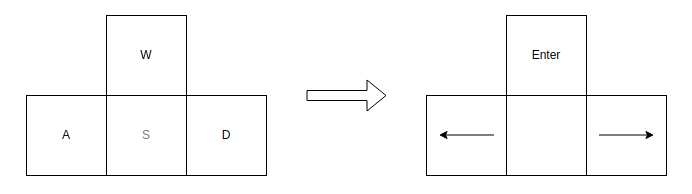
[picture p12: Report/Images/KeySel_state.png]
                
                \caption{Controls for Preset Options}
                \label{fig:keys_states}
            \end{figure}
            
            Figure \ref{fig:GUI2} shows the start screen of the GUI after selecting how the each device should be run. Notice each device window has its own mode and the white block cursor waiting on bottom near the CONFIRM button. Pressing W here will advance the GUI to data collection. Figure \ref{fig:GUI2_L} shows the color pattern of the LEDs after selecting the run modes. Notice device 1 has both blue and white LEDs while device two only has blue on. Device three still has yellow on and is put in standby or "OFF" until another cycle.
            
            \begin{figure}[H]
                \centering
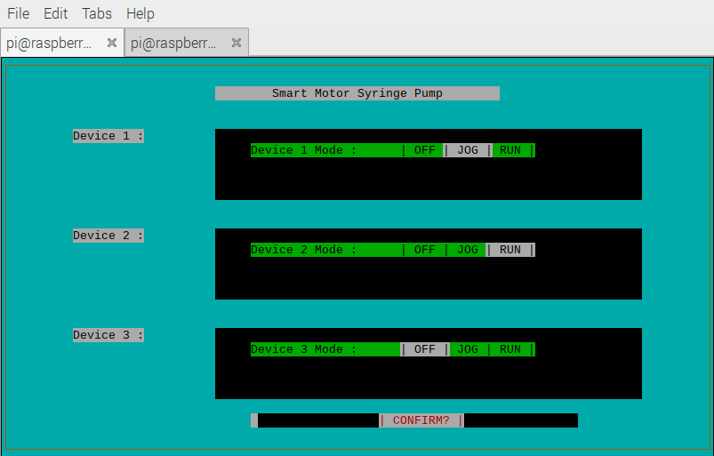
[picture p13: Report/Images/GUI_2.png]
                
                \caption{Selecting Each Run State on the Different Devices}
                \label{fig:GUI2}
            \end{figure}

            \begin{figure}[H]
                \centering
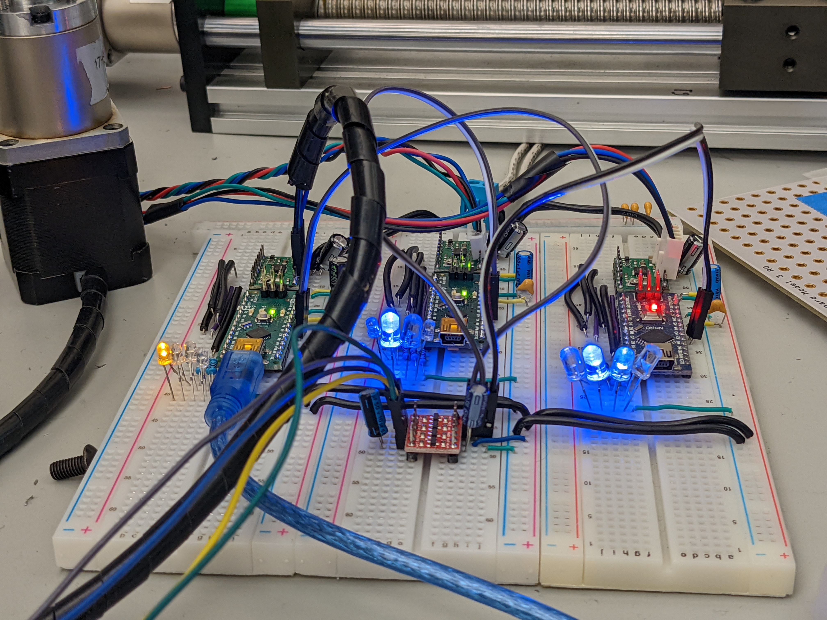
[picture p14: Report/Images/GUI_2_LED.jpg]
                
                \caption{LED Indicators for Device/State}
                \label{fig:GUI2_L}
            \end{figure}
            
            \begin{figure}[H]
                \centering
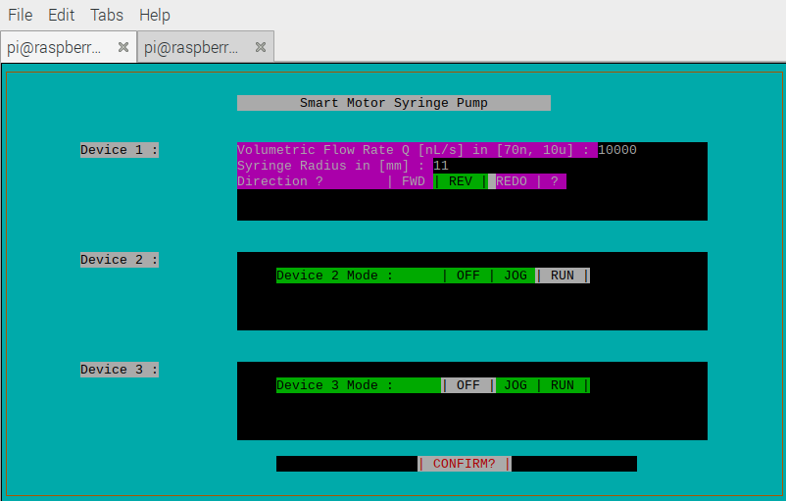
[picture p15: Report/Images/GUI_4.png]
                
                \caption{Entering User Data into the Hub Controller}
                \label{fig:GUI4}
            \end{figure}
            
            Figure \ref{fig:GUI4} gives an idea on what it would be like entering information into the hub. The GUI will prompt the user for nominal values and the user will enter then using the number keys and enter. Figure \ref{fig:key_num} illustrates the keys used when entering parameters. It should be noted that the direction of the motor is still selected using WASD. the option REDO is used to revert back to STANDBY mode for that particular device in order to reassign a run mode. Figure \ref{fig:GUI6} shows example data entered into the GUI with the CONFIRM below awaiting a W for confirmation. 
            
            \begin{figure}[H]
                \centering
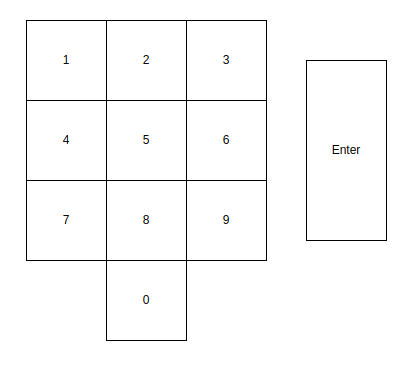
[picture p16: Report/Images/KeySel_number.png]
                
                \caption{Controls for Numerical Options}
                \label{fig:key_num}
            \end{figure}
            
            \begin{figure}[H]
                \centering
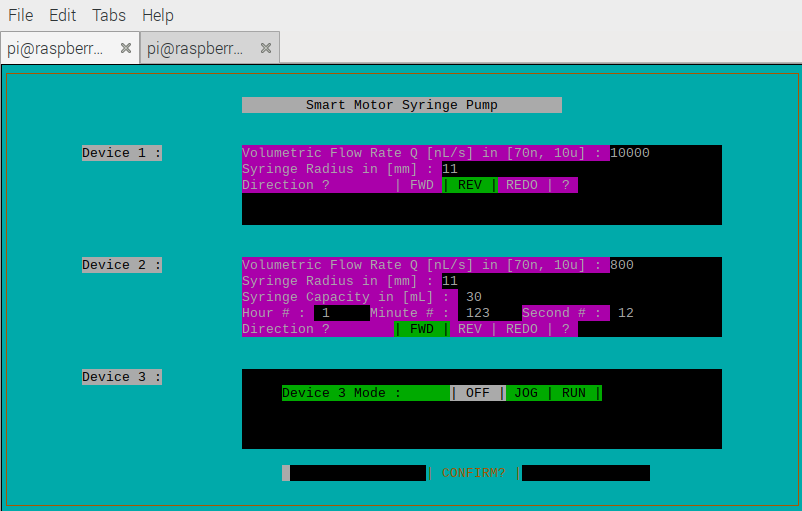
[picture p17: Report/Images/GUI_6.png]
                
                \caption{Concluding Data Pull from User}
                \label{fig:GUI6}
            \end{figure}
            
            After confirming the data pull state, the devices will enter the RUN state (Figure \ref{fig:GUI7}). The GUI will display the parameters that are being output and the time elapsed if running in run mode. Figure \ref{fig:GUI7_L} shows the LEDs for each device. Device 1 is in jog and shows green and white lights, device 2 is in run mode and only uses a green LED, and device 3 is still showing a yellow LED because it is still in standby mode. 
            
            \begin{figure}[H]
                \centering
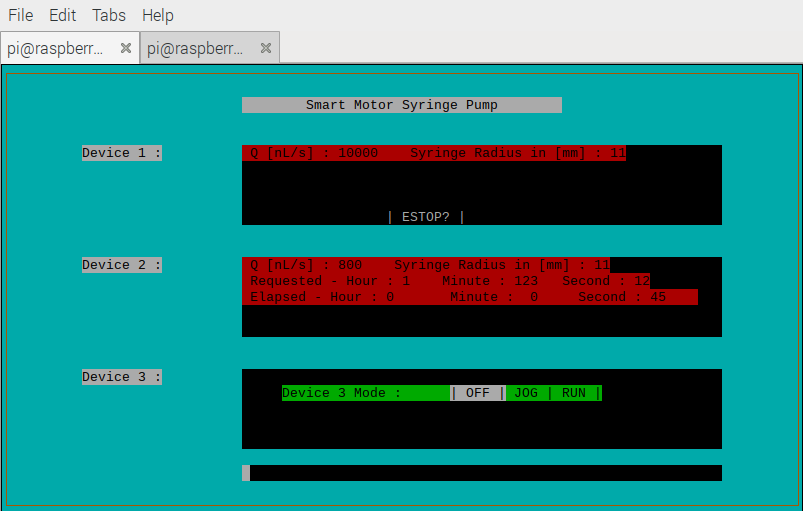
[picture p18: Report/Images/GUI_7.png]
                
                \caption{GUI Run State}
                \label{fig:GUI7}
            \end{figure}
            
            \begin{figure}[H]
                \centering
                
                \caption{LED Indicators during Run/Jog State}
                \label{fig:GUI7_L}
            \end{figure}
            
            Figure \ref{fig:GUI7}/\ref{fig:GUI9} also give information on the estop cursor. Figure \ref{fig:GUI7} shows the estop cursor on device one as "| ESTOP |" while Figure \ref{fig:GUI9} has its estop cursor at the bottom ( | ESTOP ALL? | ). The first figure will estop the device 1 only while the second figure will stop all of the devices if pressed. Figure \ref{fig:key_estop} shows the estop controls; they are using WASD but in a different order than the mode selection.   
            
            \begin{figure}[H]
                \centering
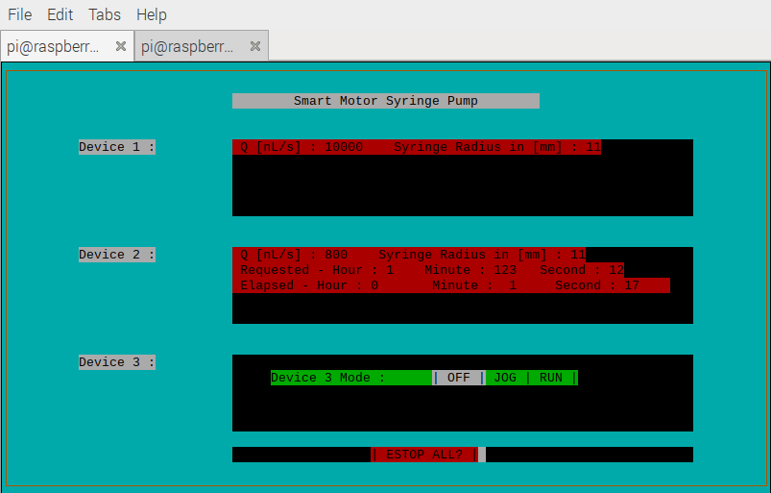
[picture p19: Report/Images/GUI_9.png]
                
                \caption{Run Screen : E-Stop All Devices}
                \label{fig:GUI9}
            \end{figure}
            
            \begin{figure}[H]
                \centering
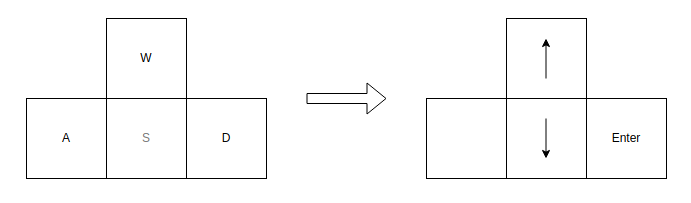
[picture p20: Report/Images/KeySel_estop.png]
                
                \caption{Controls for E-Stop}
                \label{fig:key_estop}
            \end{figure}
            
            Figure \ref{fig:GUI10} shows an example of an estop event. The estop cursor is replaced with a | STOP'D | mark, the motor haulted, and the motor controller returns to the STANDBY state as seen in Figure \ref{fig:GUI10_L}
            
            \begin{figure}[H]
                \centering
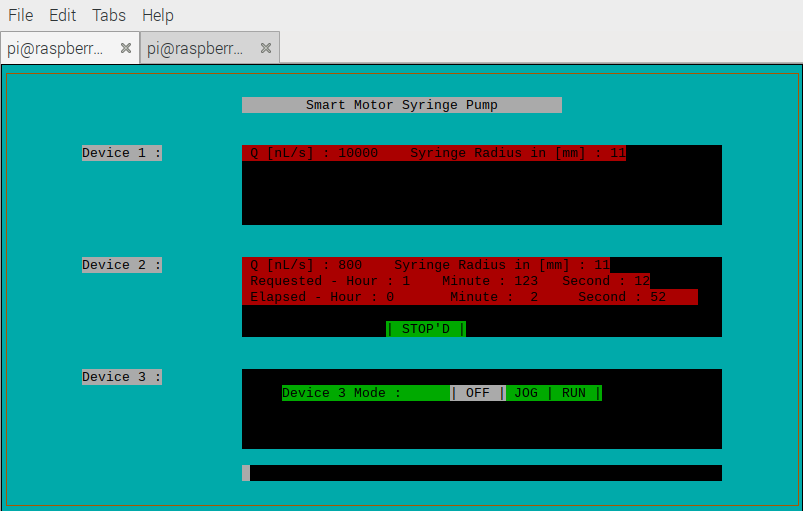
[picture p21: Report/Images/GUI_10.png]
                
                \caption{Run Screen : E-Stop Device \#2}
                \label{fig:GUI10}
            \end{figure}
            
            \begin{figure}[H]
                \centering
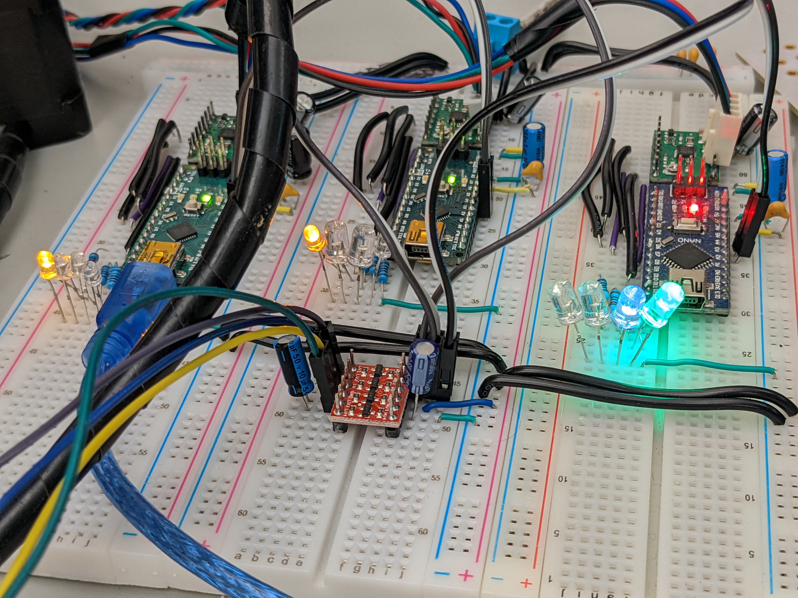
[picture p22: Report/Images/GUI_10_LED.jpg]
                
                \caption{LED Indicator with E-Stop Event}
                \label{fig:GUI10_L}
            \end{figure}
            
            The hub controller communicates with each motor controller after the user has entered in the requested parameters. No motor controller hardware is the same and as such, each user request is checked my the motor controller to see if the hardware can produce the correct output. If the requested volumetric flow rate is too large for the hardware to output, an error message will appear (Figure \ref{fig:GUI12}) and the user will be prompted to enter new parameters. Other error codes exist: Figure \ref{fig:GUI14} is too small a Q value and Figure \ref{fig:GUI15} refers to the run time exceeding the fluid capacity of the syringe. 
            
            \begin{figure}[H]
                \centering
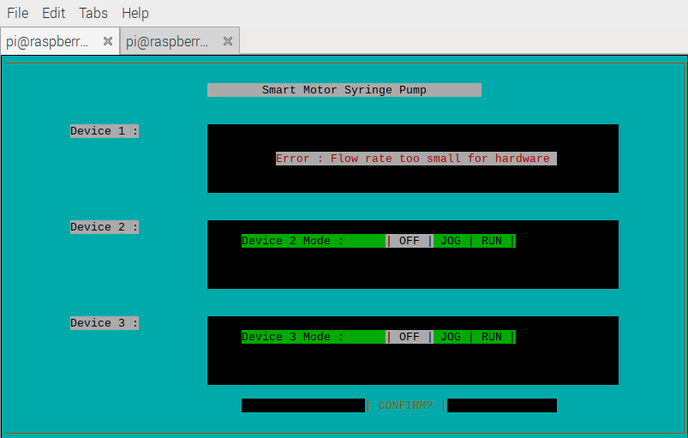
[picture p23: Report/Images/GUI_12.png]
                
                \caption{Error Code : Too Large for Hardware to Output}
                \label{fig:GUI12}
            \end{figure}
            
            \begin{figure}[H]
                \centering
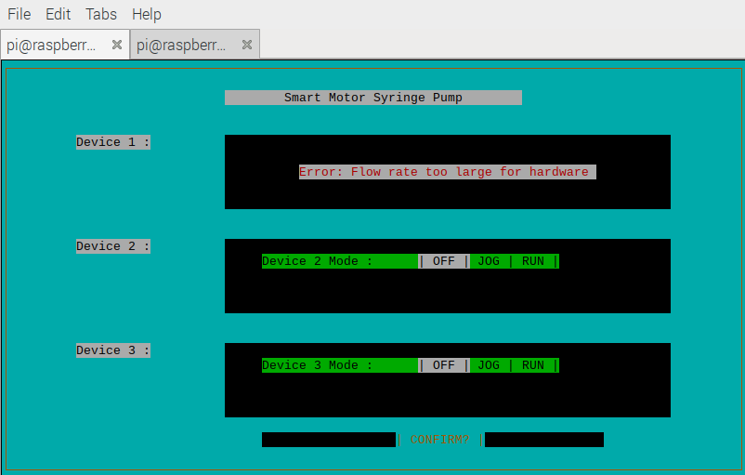
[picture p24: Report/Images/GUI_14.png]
                
                \caption{Error Code : Too Small for Hardware to Output}
                \label{fig:GUI14}
            \end{figure}
            
            \begin{figure}[H]
                \centering
                
                \caption{Error Code : Too Long for Hardware to Run}
                \label{fig:GUI15}
            \end{figure}
            %\vspace*{-2.0in}
            
            After all devices have halted, the GUI screen will return to polling for the device run mode and all of the indicator LEDs will revert back to yellow. 
            %\vspace*{-1in}
        
        \subsubsection{Logic Flow}
            This subsection discusses the logic flow of the hub controller. The python code of this controller can be seen in Appendix \ref{Appendix:Code}. 
            %\vspace*{-0.5in}
            
            Looking at Figure \ref{fig:hub0}, the hub controller has four states that it operates in: START, DATAPULL, RUN, and RESET. The START state is written to do a few items: note which devices are active on the I2C bus, reset the motor controllers to their STANDBY state, and ask the user which run mode is proper for each device. After all active devices have selected a run mode, the hub transitions to DATAPULL. DATAPULL will prompt the user for data parameters ( volumetric flow rate Q, syringe radius, syringe capacity, duration, and motor direction) and send that data to the individual motor controllers. Should the user request be outside the operating range of the hardware, the motor controller will send back an error code that will be displayed on the GUI. The program will loop until all devices are error free and the system is ready to progress into the next state. The RUN state will turn on the stepper motors and poll for a stop condition. Should the user select an estop in the GUI or the motor controller reach its max time duration, the motor controller will shut off the motor and the hub will reset for that device. After all devices have reached a stop condition, the hub will proceed to the RESET state to clear all user parameters in the hub/motor controllers. The hub will return to the START state and STANDBY in the motor controllers. 
            
            It should be noted that the GUI referenced in the previous subsection is the same here and can be referenced as such. 
            
            \begin{figure}[H]
                \centering
                
                \caption{Top Level Flow Chart of Hub Controller}
                \label{fig:hub0}
            \end{figure}

    \subsection{Motor Controller}
        This subsection discusses an individual motor controller in the SMSS in three different sub-sub-sections. The first will discuss the characterization of the system, the second will map the control flow, and lastly there is a section about the I2C communication between the hub and motor controllers.
        
            \subsubsection{Plant Characterization}
                Starting with the syringe, the mechanical conversion that takes place in the syringe is as follows in Figure \ref{fig:q2v}. The volume of fluid displaced by the syringe plunger is proportional to the speed at which the plunger is moving. This plunger speed (V) is applied across the plunger's surface area, producing a volumetric flow \( \frac{m^3}{sec}\). This unit can be converted to \( \frac{L}{sec}\) with unit conversion.
                
                \begin{figure}[H]
                    \centering
                    
                    \caption{Components of a Syringe}
                    \label{fig:syringe}
                \end{figure}
                
                \begin{figure}[H]
                    \centering
                    
                    \caption{Plant Conversion of Syringe}
                    \label{fig:q2v}
                \end{figure}

               After understanding how the linear velocity V is translated into a volumetric flow rate Q, lets discuss how the gearbox's RPM is converted into a linear velocity. Figure \ref{fig:rot2lin} illustrates how the RPM from the gearbox is translated to a linear velocity on the syringe plunger. The gearbox shaft is coupled to the screw rod at a 1 to 1 ratio; this segment does not require further analysis as no slip was witnessed. The interaction of the screw rod and the pillow block does however : the pillow block is attached to the frame of the ball screw kit and must be engaged with the screw rod to move. The helical spiral in Figure \ref{fig:helix} represents the screw rod that engages with the threaded bearing in the pillow block. The linear speed of the pillow block is dependant on the the rotational speed as well as a few factors. The position of a single particle on the helix is represented as r(t), with respect to time. 

               \begin{figure}[h]
                    \centering
                    
                    \caption{Translation of Angular Velocity to Linear Velocity}
                    \label{fig:rot2lin}
                \end{figure}
                
                \begin{figure}[h]
                    \centering
                    
                    \caption{Cylindrical Helix Model for Ball Screw}
                    \label{fig:helix}
                \end{figure}
                
                \begin{equation}
                    \begin{split}
                        Let\,\, r(t) = \rho \cos(\overrightarrow{\omega_g}t)\,\hat{\mathbb{A}}_x + 
                                        \rho \sin(\overrightarrow{\omega_g}t)\,\hat{\mathbb{A}}_y +
                                        \gamma \overrightarrow{\omega_g}t\,\hat{\mathbb{A}}_z \,\,\,\,\,\,\left [m\right]
                    \end{split}
                \end{equation}
                                
                Where \(\rho\) is the screw rod radius and \(\gamma\) is the rod's pitch. The rod's pitch is the z-axis distance between points of the same xy angle.
                
                To find the velocity of the particle with respect to time, the derivative of r(t) is taken.
                \begin{equation}
                    \begin{split}
                         \overrightarrow{v}(t) = \frac{d}{dt}\, r(t) \,\,\,\,\,\,\left [\frac{m}{s}\right]
                    \end{split}
                \end{equation}

                \begin{equation}
                    \begin{split}
                        \scriptsize{
                        \overrightarrow{v}(t) = - \rho \overrightarrow{\omega_g} \sin(\overrightarrow{\omega_g}t)\,\hat{\mathbb{A}}_x + 
                        \rho \overrightarrow{\omega_g} \cos(\overrightarrow{\omega_g}t)\,\hat{\mathbb{A}}_y + 
                        \gamma \overrightarrow{\omega_g} \,\hat{\mathbb{A}}_z
                        \,\,\,\,\,\,\left [\frac{m}{s}\right]}
                    \end{split}
                \end{equation}
                
                Focusing attention on the Z-axis movement :
                
                \begin{equation}
                    \begin{split}
                        {\overrightarrow{v_z}(t)} &= \gamma \overrightarrow{\omega_g} \,\,\,\,\,\,\left [\frac{m}{s}\right] \\
                        \overrightarrow{\omega_g} &= \frac{{\overrightarrow{v_z}(t)}}{\gamma}
                        \,\,\,\,\,\,\left [\frac{rad}{s}\right] \\
                        {\overrightarrow{RPM}}_{gearbox}(t) &= \frac{2\pi {\overrightarrow{v_z}(t)}}{\gamma}
                        \,\,\,\,\,\,\left [\frac{Rev}{s}\right]
                    \end{split}
                \end{equation}
                
                The final equation relates the rotational speed of the gearbox to the linear velocity of the pillow block. Figure \ref{fig:rps_2_Q} is the plant of the system from this point. From here, relating individual steps of the stepper motor to the output RPS is the final step in characterizing the system. The STSPIN820 motor driver can output up to 256 microsteps, allowing the driver to further divide the input PWM freq at the cost of motor torque \cite{stepper_theory}. The stepper motor itself markets 200 steps per revolution; both motor step and the driver's microstep will alter the motor's speed. Figure \ref{fig:total_hard} depicts the addition of both step properties as well as the final representation of the hardware system.   
                
                \begin{figure}[H]
                    \centering
                    
                    \caption{Translation of Motor Speed to Flow Rate}
                    \label{fig:rps_2_Q}
                \end{figure}
                
                \begin{figure}[H]
                    \centering
                    
                    \caption{Complete Hardware Characterization of Pump}
                    \label{fig:total_hard}
                \end{figure}
                
                Working backward to find the appropriate frequency, \(f_{user}\) can be defined as : 
                \begin{equation}
                    \begin{split}
                        f_{user} &= X_m * \frac{400\pi N Q}{1000\gamma \pi r^2 }\\
                         &= X_m * \frac{2 N Q}{5\gamma r^2 }
                     \end{split}
                \end{equation}
                where N is the gear ratio, \(\gamma\) is the pitch of the ball screw, \(X_m\) is the microstep divisor, \(f_{user}\) is the frequency derived from the user requested Q, and r is the radius of the syringe plunger.
                
                From experimentation, it was found that the minimum frequency the stepper motor should operate at or above is 120 Hz (\(f_{min} = 120Hz\)). With this standard, finding the proper microstep size is a simple equation : 
                
                \begin{equation}
                    \begin{split}
                        f_{user} &\geq f_{min}\\ 
                        X_m * \frac{2 N Q}{5\gamma r^2 } &\geq f_{min}\\
                        X_m &\geq \frac{f_{min}}{\frac{2 N Q}{5\gamma r^2 }}\\
                        \therefore X_m &\geq \frac{5 \gamma r^2 f_{min}}{2NQ}
                    \end{split}
                \end{equation}
                
                The range of Q is limited to the frequency range of the stepper motor and was found experimentally as well. Both maximum and minimum Q values would stall the stepper motor. It was also noticed that frequencies above and below the range could move the motor but not reliably. The reliable range is : 
                
                \[ Q \,\,\in \,\,[10n, 16\mu] \,\,\,\, \left [\frac{L}{sec} \right ]\]
                
            \subsubsection{\hl{Control Flow}}
                The individual pump/motor controllers have the same code structure but can have different hardware parameters (syringe radius, ball screw radius, etc). Moreover, each controller can be placed into a I2C mode - the hub controller will dictate the flow of user info, or in serial mode - the Arduino IDE serial terminal will prompt the user for information. It should be noted that the serial method is device specific and wont control more than one pump controller. The serial mode is also referred as manual mode because it is easy to tune parameters for an individual pump without the use of an additional controller. To use either mode, comment out the unused setting as in Figure \ref{fig:comments}. 
                
                Both modes of the motor controller use different communication protocols but are similar in state structure. Figure \ref{fig:motor0} represents the highest level of flow for the motor controller : 6 states that will continue to loop until power is cycled. The controller will start and stay in STANDBY until the controller has received a START/JOG request. After leaving, the controller will go in to either DATAPULL\_S (for timed duration) or DATAPULL\_J (for jog) to retrieve the hardware parameters from the user. This data can be from I2C or serial depending on which portion of code had been enabled. After checking for errors, the device will proceed to the appropriate RUN state. Once the device has received an ESTOP or time-dependent FINISH command, the device will reset all variables in ESTOP and proceed to wait in STANDBY. This top level is almost identical to the hub controller but has many lower level differences. 
                
                Lower level flow charting can be found in Appendix \ref{Appendix:Documents}.

                \begin{figure}[H]
                    \centering
                    
                    \caption{Tool selection for the Motor Controller}
                    \label{fig:comments}
                \end{figure}

                \begin{figure}[H]
                    \centering
                    
                    \caption{Top Level Flow Chart of Motor Controller}
                    \label{fig:motor0}
                \end{figure}

            \subsubsection{I2C Communication Between Controllers}
                The hub controller assumes the position of the main device with the pump controllers acting as sub devices. The sub devices don't communicate with each other; only the hub controller sends a receive (MOSI) or request (MISO) command. The hub controller is a raspberry pi,  which a logic high of 3.3V, and the pump controller, arduino nano, has a logic high of 5v. With a difference in logic level voltage, a bi-directional logic converter was used in order for the devices to communicate to each other without hardware damage. For simplicity, a Sparkfun MOSFET converter was used as seen in the Appendix \ref{Appendix:Documents} schematics. 
                
                The data sent and requested by the main controller was often over the single packet 255 bit limit. To overcome this, data packets are processed to handle numbers less than 16,777,215. This is done by sending factors that are multiplied by 256 as well as remainders that are summed with the total number. The trade off for this solution is the extra time it takes to transmit three extra packets of information.  

                If the number is large enough to fill the second factor,
                \[ Number = 256 * (256 Fact_2 + Remain_2) + Remain_1\]
                
                else :
                \[ Number = 256 Fact_1 + Remain_1\]
                
                where each variable above represents a single packet.

\section{Testing}
        This section outlines the process for verifying the engineering requirements (Table \ref{table:EngineeringReq}) of the SMSS. The financial requirement, keeping the SMSS under \$500 USD is verifiable by viewing the Bill of Materials in Appendix \ref{Appendix:Documents} Figure \ref{fig:BoM}. This requirement is met for this generation of the SMSS because the cost was under \$500 USD. 
        
        The second and third requirement will be validated in the next section below; the fourth requirement can be verified by noting the libraries and hardware used. The code (Appendix \ref{Appendix:Code}) that was used is open source online and the hardware is not locked by physical/digital means. Both Arduino and Raspberry Pi devices are designed to be altered down to the copper or the kernel. 
        
        The fifth requirement was verified visually by inserting different syringes into the housing. The recorded range of syringes was 1mL to 30mL, going beyond the requirement. 
        
        Requirement six, concerning 3 pump controllers, is also verified in the subsection below. That requirement requests an analysis of three separate devices and their output flow rate. 
        
        Requirement seven is the GUI requirement and it is met by viewing the hub controller section earlier on in the paper. 
        
        Requirement eight, requesting that the drive train and pump housing be 3D printed, has fallen short of its goal. The drive train is a metallic ball screw that must be metal for friction and wear purposes. 3D printing this piece would require additional work for a lesser component. The housing of the entire system has also yet to be 3D printed because the footprint of the SMSS will continue to decrease. It was not fit to enclose the entire system at this stage of prototyping. Printing a piece that hold the ball screw and syringe together has proved to be a value component in this stage of the SMSS. 
        
        The last requirement was also short of its goal. This generation of the SMSS was unable to integrate viable feedback in the system. Different feedback methods (potentiometers, resolvers, pressure sensors) were considered but were left out due to budget and time constraints. Without feedback, output data couldn't be produced and sent to the hub controller. 
        
    \subsection{Verification Method for Hardware}
        The output flow rate of the SMSS was measured with a LabSmith uProcess kit. This kit measures the pressure inside a CapTile cavity and was the only method used. To use this device properly, the user must setup the device as shown in Figure \ref{fig:verif_diagram} and note physical measurements of the differential tubing. This tube's inner diameter and length are important in translating the pressure measurement into a measured volumetric flow rate. While the SMSS is applying pressure on the plunger of the syringe, water is flowing through the filter and into the three-way CapTile. The uPOS senor then measures the pressure at its highest potential at the intersection in reference to the lowest potential point at the other end of the differential tube. The pressure across the differential tube is the measured result \( \triangle P   \,\,\,\, [kPa]  \). The change in pressure can be translated into a volumetric flow rate with the following equation. It should be noted that the GUI has Q in terms of nL/sec, hence the conversion to nL/s here.
        
        \begin{equation}
            \begin{split}
                \triangle P &= P_{meas} - P_{atm} \,\,\,\,\,\,\,\, [kPa] \\
                &\approx  P_{meas} - 1 \,\,\,\,\,\,\,\,\,\,\,\, [kPa]
            \end{split}
        \end{equation}

        \begin{equation}
            \begin{split}
                Q_{deriv} &= \frac{\pi \,\,(\triangle P) \,\,D^4}{128 \mu \,\,\mathbb{L}}  \,\,\,\,\left[\frac{m^3}{sec}\right]\\
                &= \frac{\pi \,\,(\triangle P) \,\,D^4}{128 \mu \,\,\mathbb{L}} * \frac{10^3 L}{m^3} * \frac{10^9 nL}{L} * \frac{10^3 Pa}{kPa} \,\,\,\,\left[\frac{nL}{sec}\right]\\
                \therefore &= \frac{\pi \,\,(\triangle P) \,\,D^4}{128 \mu \,\,\mathbb{L}} * 10^{15}  \,\,\,\,\left[\frac{nL}{sec}\right]
            \end{split}
        \end{equation}
        
        where
        \begin{itemize}
            \item \(\triangle P \) is the change is pressure measured by the uPOS (kPa)
            \item D is the inner diameter of the differential tube (m)
            \item \( \mu \) is the dynamic fluid viscosity of water at 21 C (Pa * sec)
            \item $\mathbb{L}$ is the length of the differential tube for which the pressure change takes place (m).
            \item \( Q_{deriv}\) is the volumetric flow rate derived from the change in pressure measurement (nL/sec). This variable will be compared with the Q value entered by the user in the GUI. 
        \end{itemize}
        
        \begin{figure}[H]
            \centering
            
            \caption{Verification Model}
            \label{fig:verif_diagram}
        \end{figure}
        
    \subsection{Results}
        Using the setup in the sub-section above, a variety of nominal values were sampled. This method was used to experimentally find the operating range of the SMSS.
        
        \subsubsection{Ceiling of Q Range}
            The ceiling of an individual syringe pump was initially verified visually by witnessing the spin of the motor while coupled with a syringe. Later in the project, this was properly verified using the uProcess kit. All other values above 16\(\mu L\)/sec were not repeatable and ended up stalling the motor. It should be noted that this real max value of 16\(\mu L\)/sec is far below the set engineering requirement; below both the maximum and minimum requirement. Here are the results :
            
            \begin{table}[H]
                \renewcommand{\arraystretch}{1.3}
                \caption{Parameters of Ceiling Test}
                \label{table:test_param_ceiling}
                    \begin{center}
                        \begin{tabular}{|c|c|c|}
                            \hline
                            \bfseries Variable&
                            \bfseries Value&
                            \bfseries Unit
                            \\ \hline
                            
                            Syringe \#&
                            S1&
                            -
                            \\ \hline
                            
                            Motor \#&
                            M1&
                            -
                            \\ \hline
                            
                            Arduino \#&
                            A1&
                            -
                            \\ \hline
                            
                            Motor Controller \#&
                            STSPIN820&
                            -
                            \\ \hline
                            
                            Sensor&
                            uPOS250-T116&
                            -
                            \\ \hline
                            
                            Pipe Length \(\mathbb{L}\) &
                            0.0820&
                            m
                            \\ \hline
                            
                            Pipe Inner Dia D&
                            0.15&
                            mm
                            \\ \hline
                            
                            Dynamic Fluid Viscosity \(\mu\) &
                            0.000975 @ \(20^\circ\)C&
                            Pa*sec
                            \\ \hline

                            Syringe Radius(GUI)&
                            11&
                            mm
                            \\ \hline
                            
                            Motor Direction&
                            Forward&
                            -
                            \\ \hline
                            
                        \end{tabular}
                    \end{center}
                \end{table}

                \begin{figure}[H]
                    \centering
                    
                    \caption{Coarse Measurement for Nominal Q : 16000 nL/sec}
                    \label{fig:T2_coarse}
                \end{figure}
                
                \begin{figure}[H]
                    \centering
                    
                    \caption{Fine Measurement for Nominal Q : 16000 nL/sec}
                    \label{fig:T2_fine}
                \end{figure}
                
                Figure \ref{fig:T2_coarse} is the entire capture of processed data. There is an exponential rise to 16000 nL/sec and it holds around that number until the pump is turned off, near 150 seconds. The coarse figure appears to hit and stay on the nominal value however, Figure \ref{fig:T2_fine} shows differently. The same value lines are present but the measured result is oscillating around the nominal value. It should be noted that the water flowing out of the differential tube is jet-like and not droplets.
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

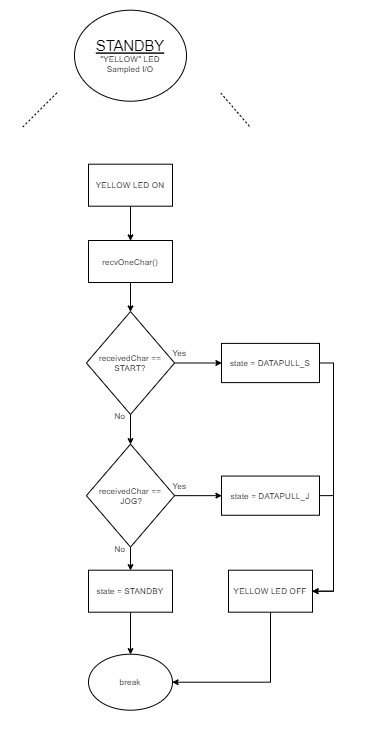
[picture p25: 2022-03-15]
Report/Images/STANDBY_ver1.jpg

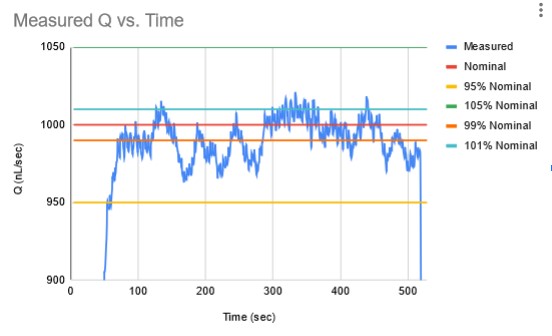
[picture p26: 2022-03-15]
Report/Images/T8.jpg

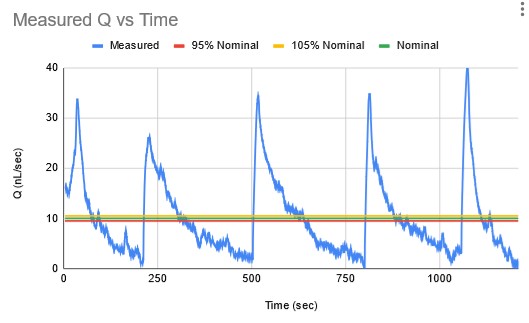
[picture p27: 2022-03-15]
Report/Images/T4.jpg

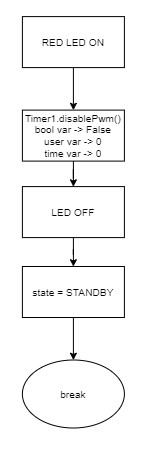
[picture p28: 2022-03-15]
Report/Images/STOP_ver1.jpg

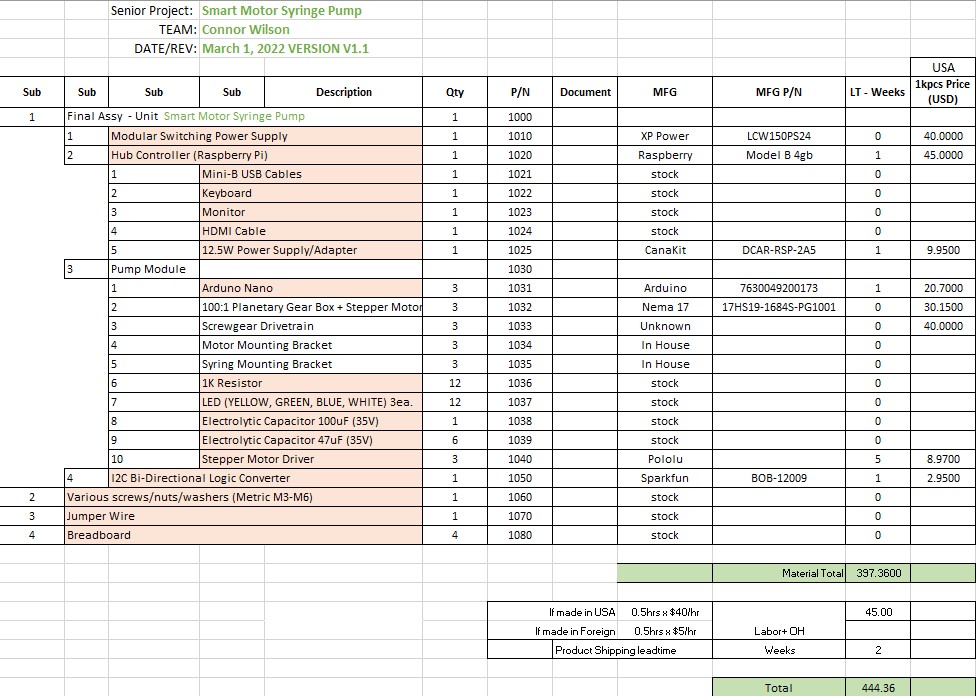
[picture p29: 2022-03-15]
Report/Images/BoM.jpg

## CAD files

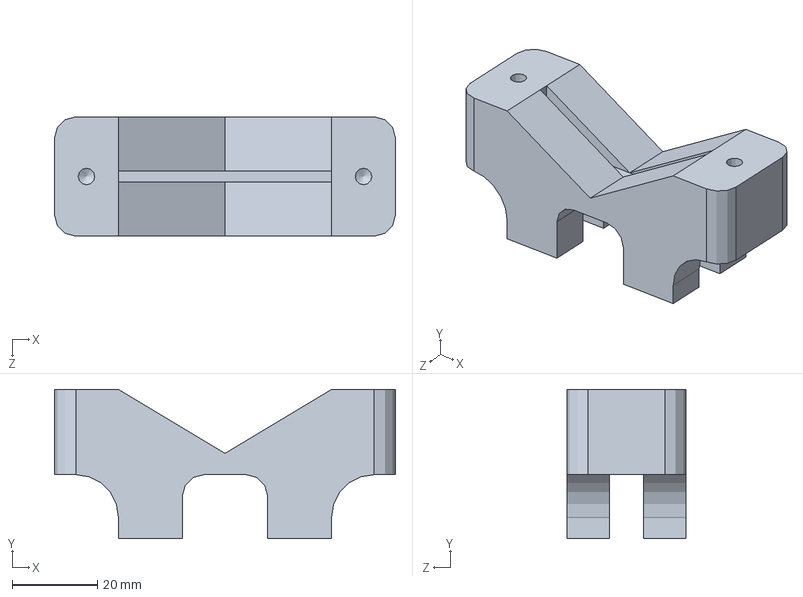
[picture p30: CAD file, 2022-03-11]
3D_parts/1205/Small_Finger_Flange_holder.SLDPRT
80.0 x 35.0 x 28.0 mm

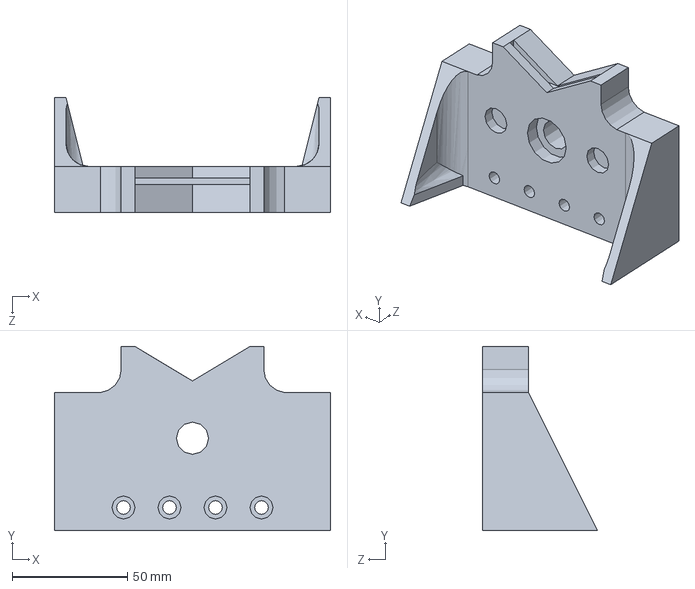
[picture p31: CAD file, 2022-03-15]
3D_parts/1605/backplate_winter2022.SLDPRT
120.0 x 80.0 x 50.0 mm

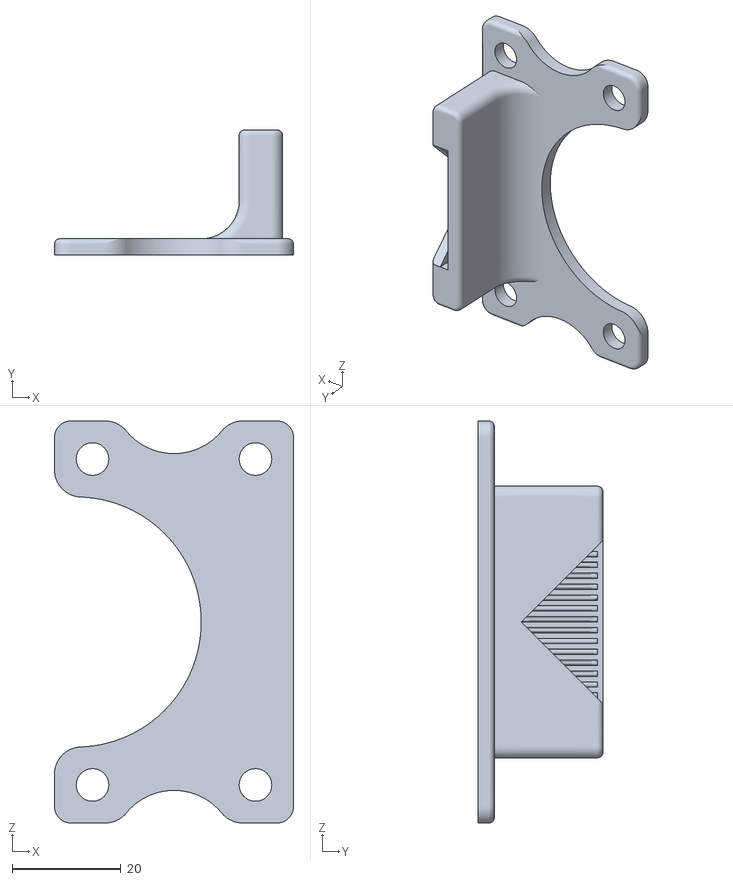
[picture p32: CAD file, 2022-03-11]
3D_parts/1605/syringe pump holder.stl
44.0 x 23.0 x 74.0

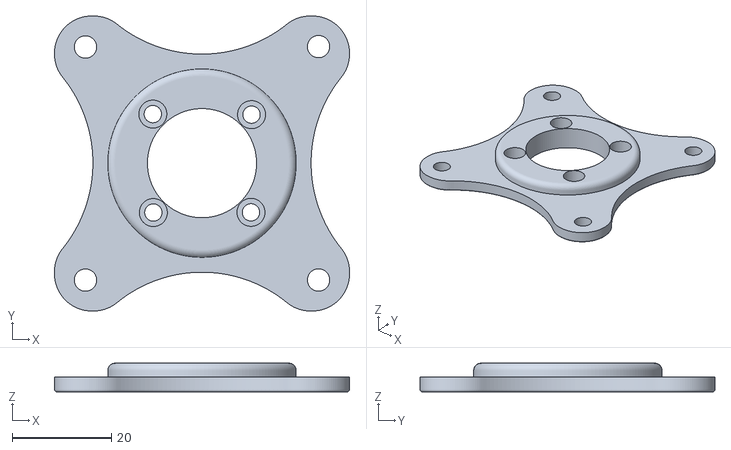
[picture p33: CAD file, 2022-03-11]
3D_parts/1605/worm gear mountV2.stl
59.5 x 59.5 x 5.80

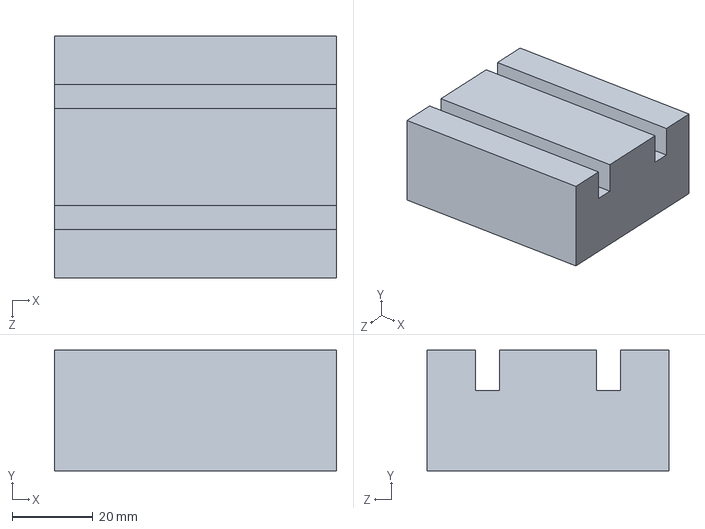
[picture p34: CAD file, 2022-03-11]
3D_parts/1205/BallScrew_guide/PillowBlock.SLDPRT
70.0 x 30.0 x 60.0 mm

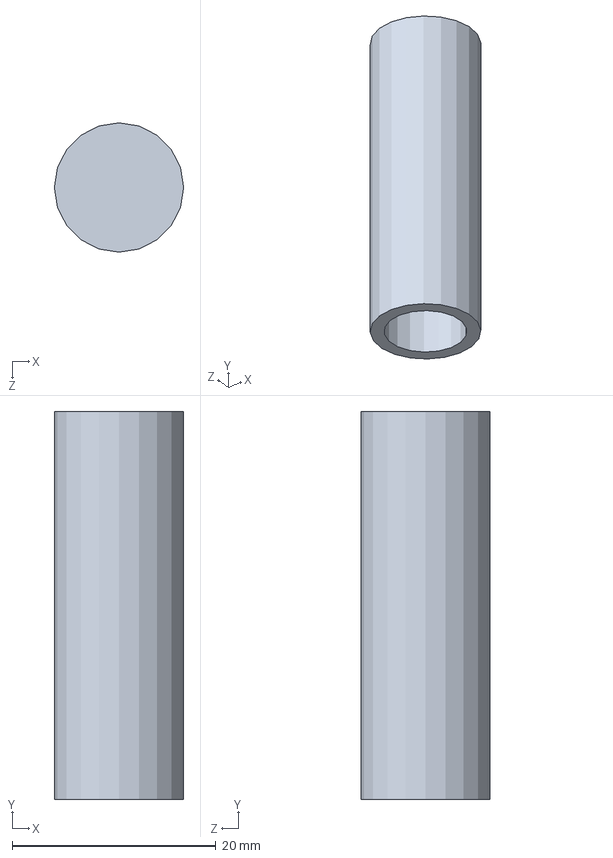
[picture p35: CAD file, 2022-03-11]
3D_parts/1205/BallScrew_guide/BallScrewGuide.SLDPRT
12.7 x 38.1 x 12.7 mm

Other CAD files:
3D_parts/1605/backplate.dwg
3D_parts/1205/BallScrew_guide/BallScrewGuide.STL
3D_parts/1205/Small_Finger_Flange_holder.SLDDRW
3D_parts/1205/Small_Finger_Flange_holder.STL
3D_parts/1605/backplate_winter2022.SLDDRW
3D_parts/1605/backplate_winter2022.STL
3D_parts/1605/syringe pump holder.ipt
3D_parts/1605/worm gear mountV2.ipt

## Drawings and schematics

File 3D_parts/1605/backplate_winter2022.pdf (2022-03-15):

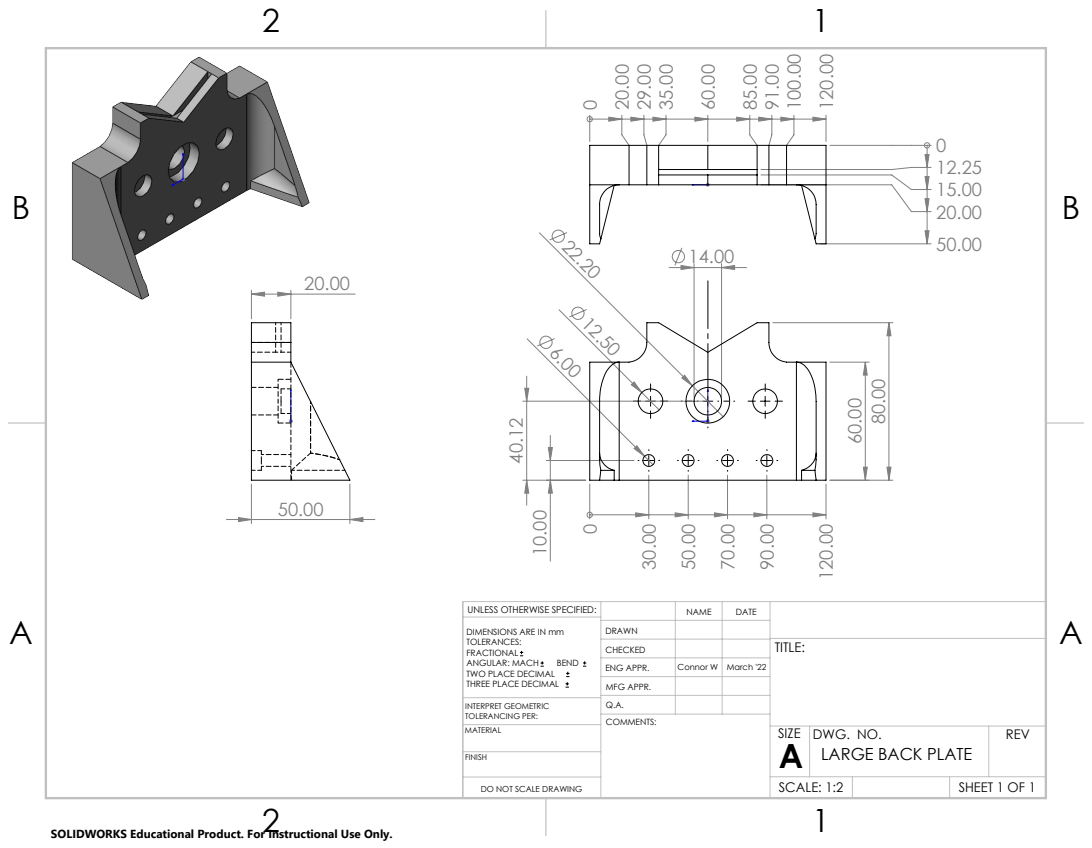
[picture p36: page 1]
DO NOT SCALE DRAWING; SCALE: 1:2; SHEET 1 OF 1

UNLESS OTHERWISE SPECIFIED: | | NAME | DATE
DIMENSIONS ARE IN mm TOLERANCES: FRACTIONAL ANGULAR: MACH BEND TWO PLACE DECIMAL THREE PLACE DECIMAL | DRAWN

CHECKED | | | TITLE:

ENG APPR. | Connor W | March '22
MFG APPR.

INTERPRET GEOMETRIC TOLERANCING PER: | Q.A.

SIZE
DWG. NO.
LARGE BACK PLATE

SOLIDWORKS Educational Product. For Instructional Use Only.

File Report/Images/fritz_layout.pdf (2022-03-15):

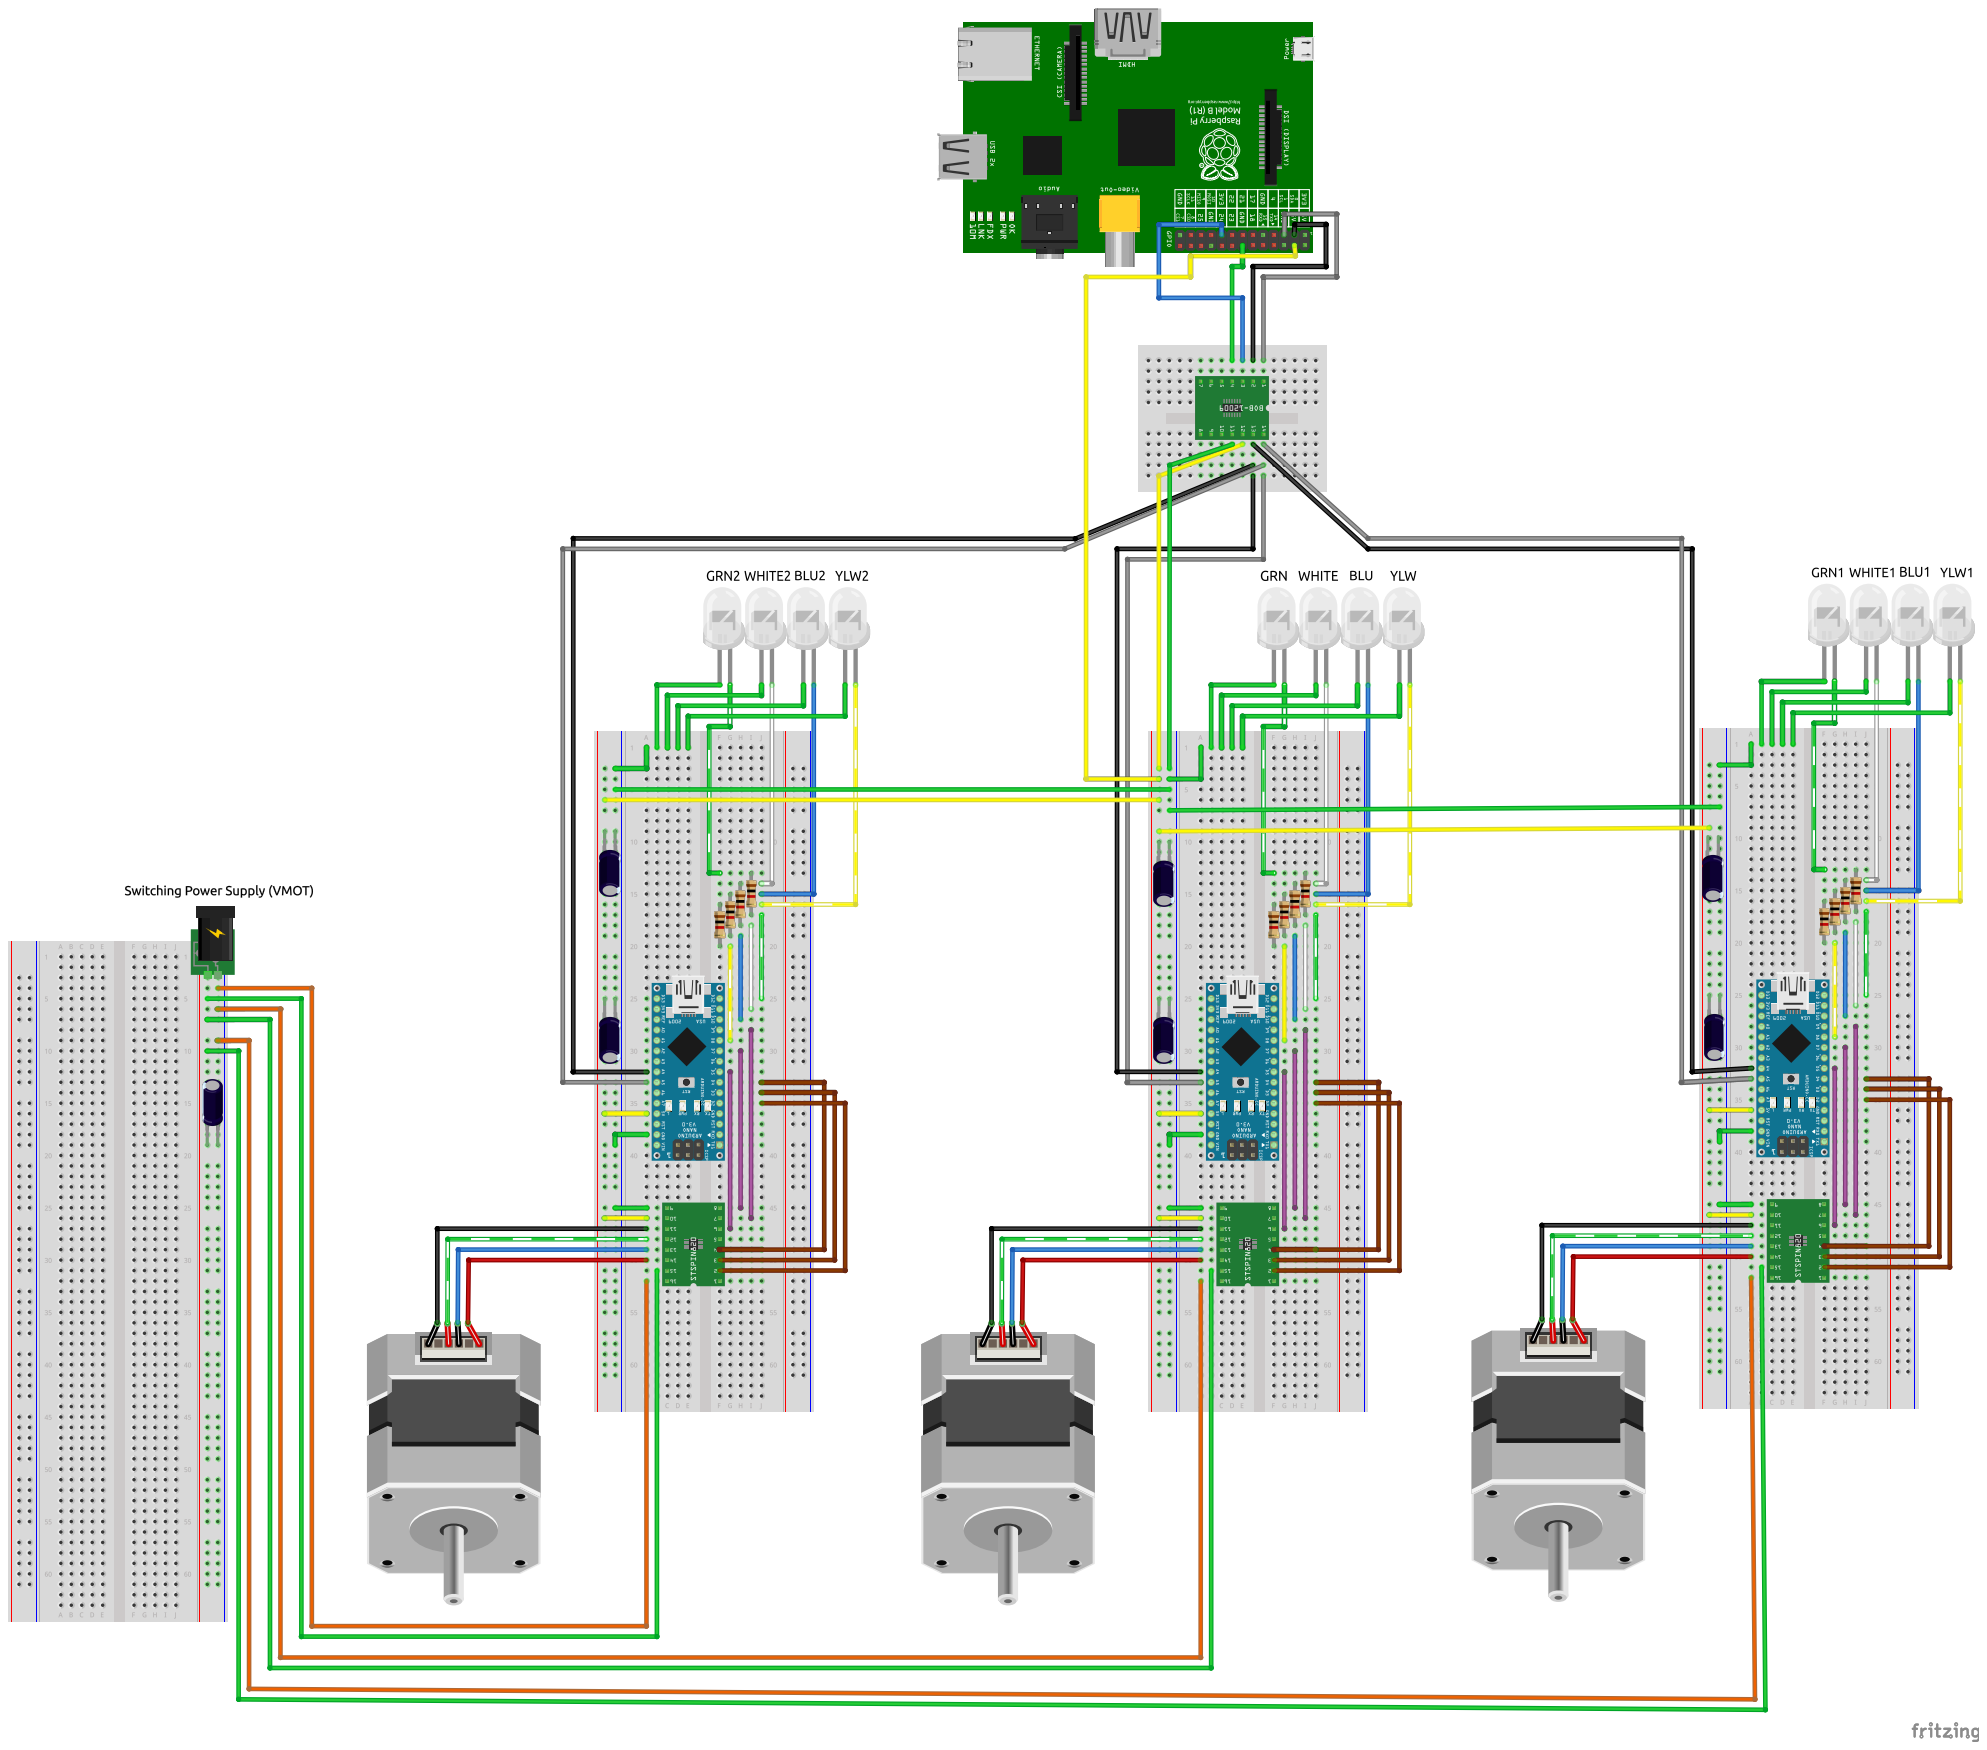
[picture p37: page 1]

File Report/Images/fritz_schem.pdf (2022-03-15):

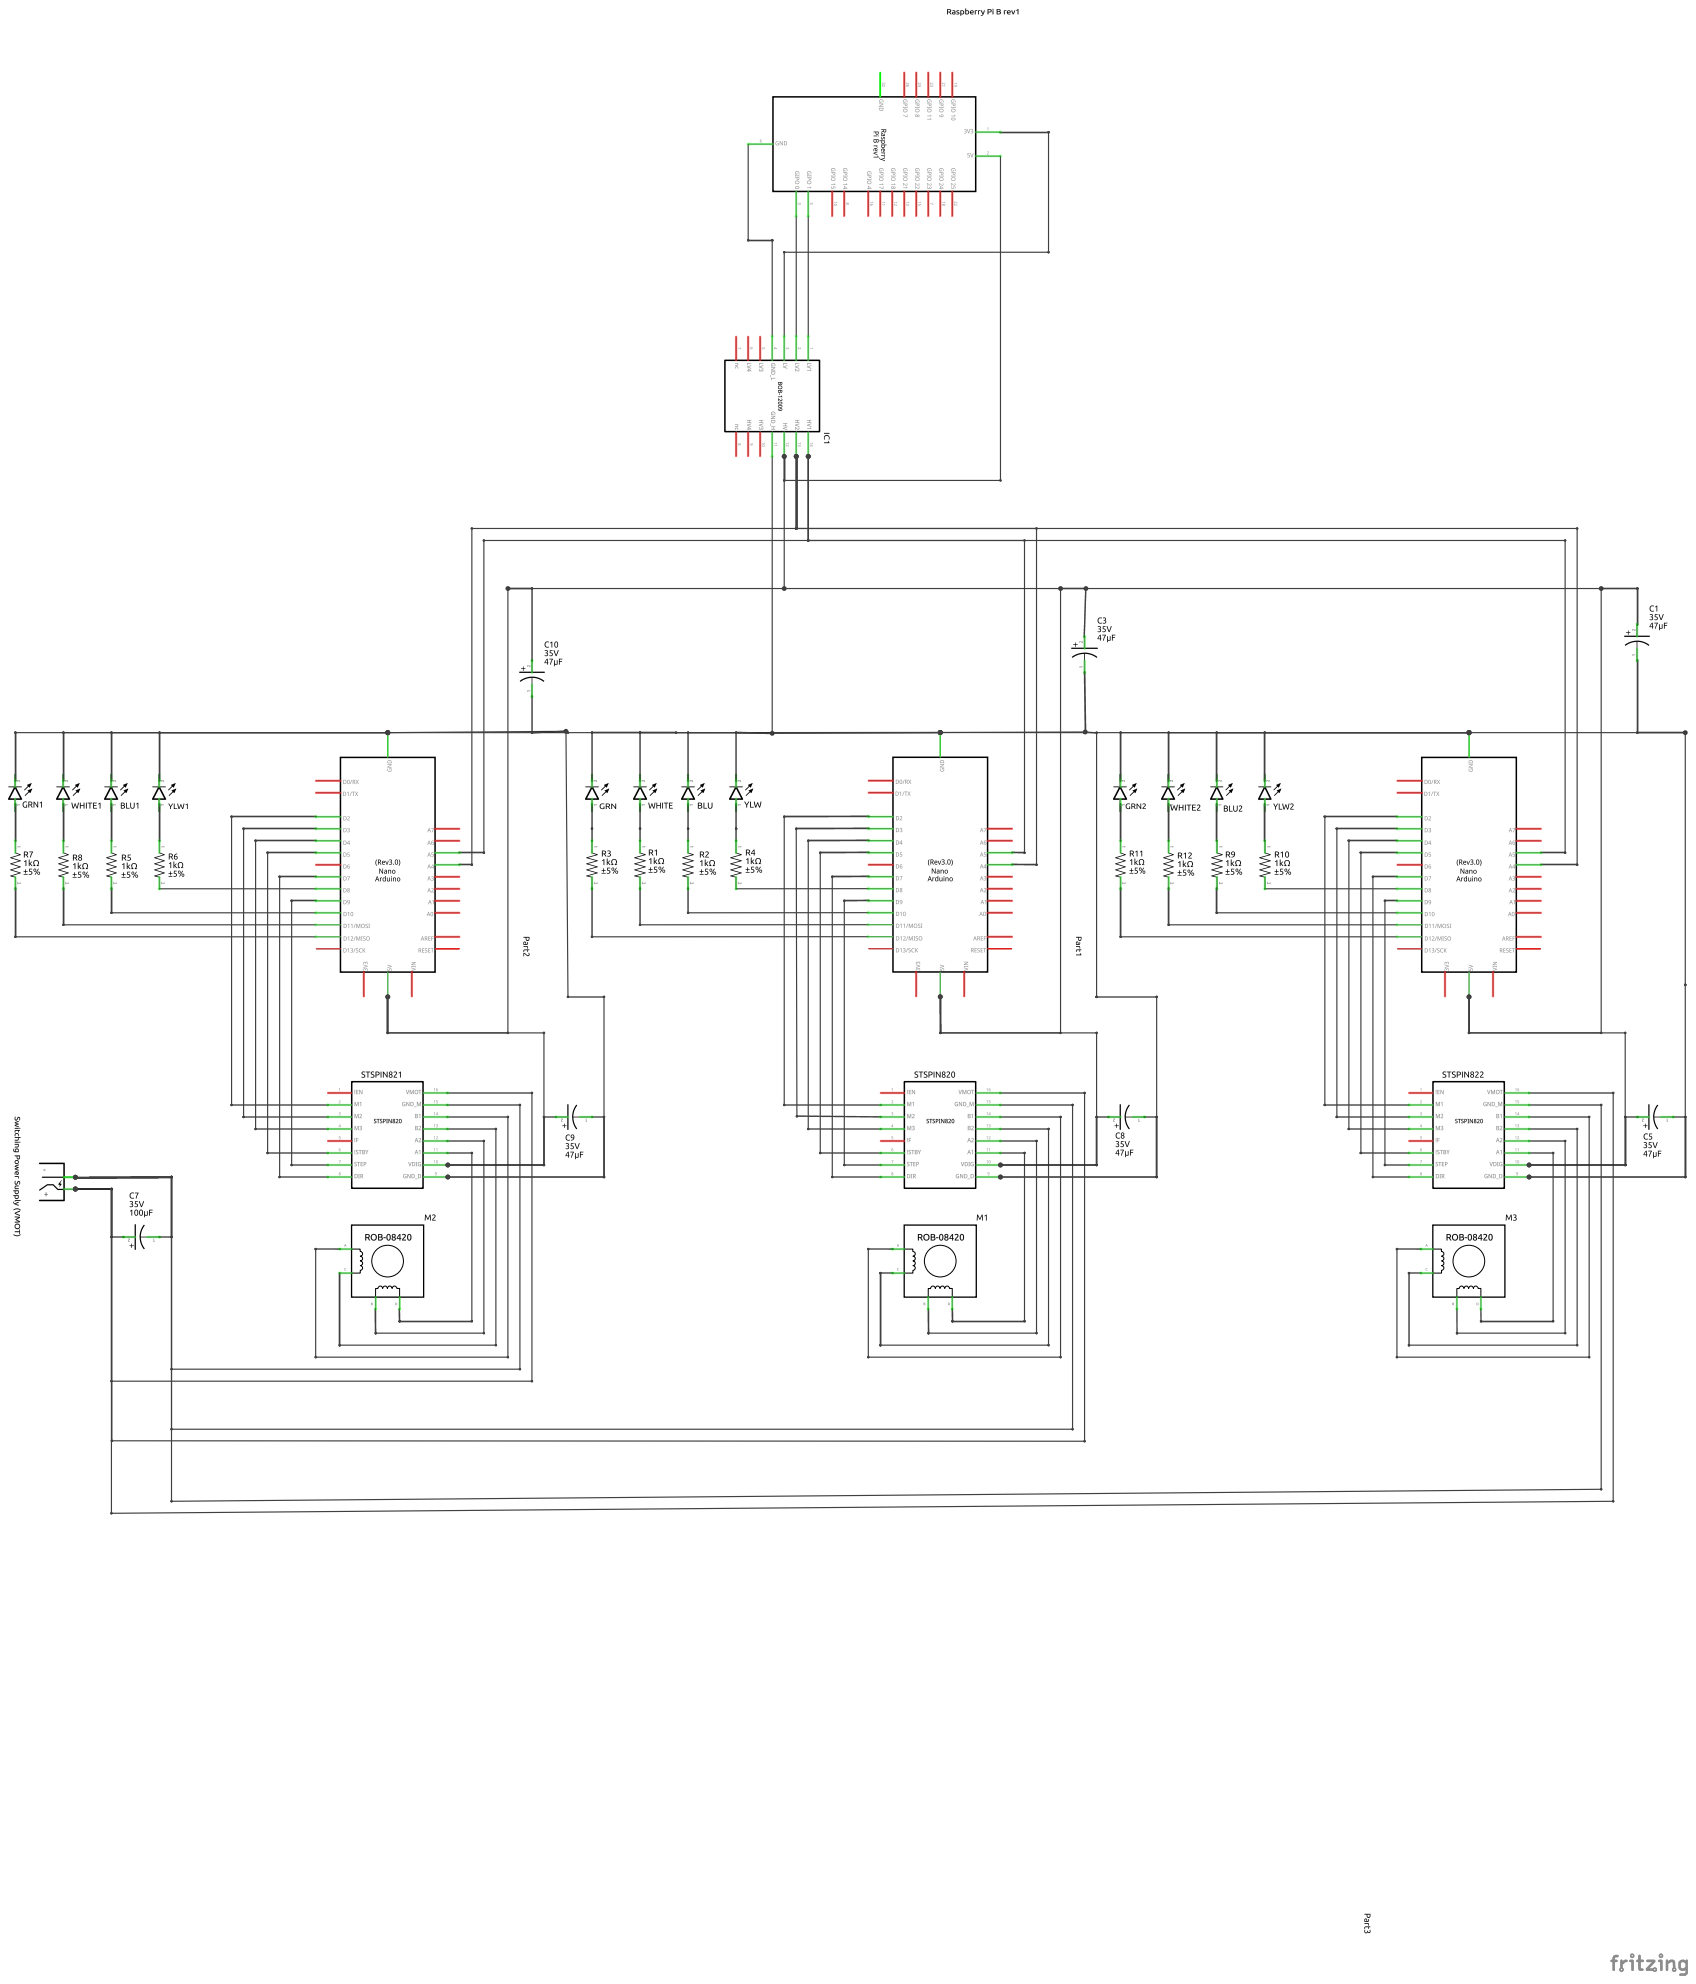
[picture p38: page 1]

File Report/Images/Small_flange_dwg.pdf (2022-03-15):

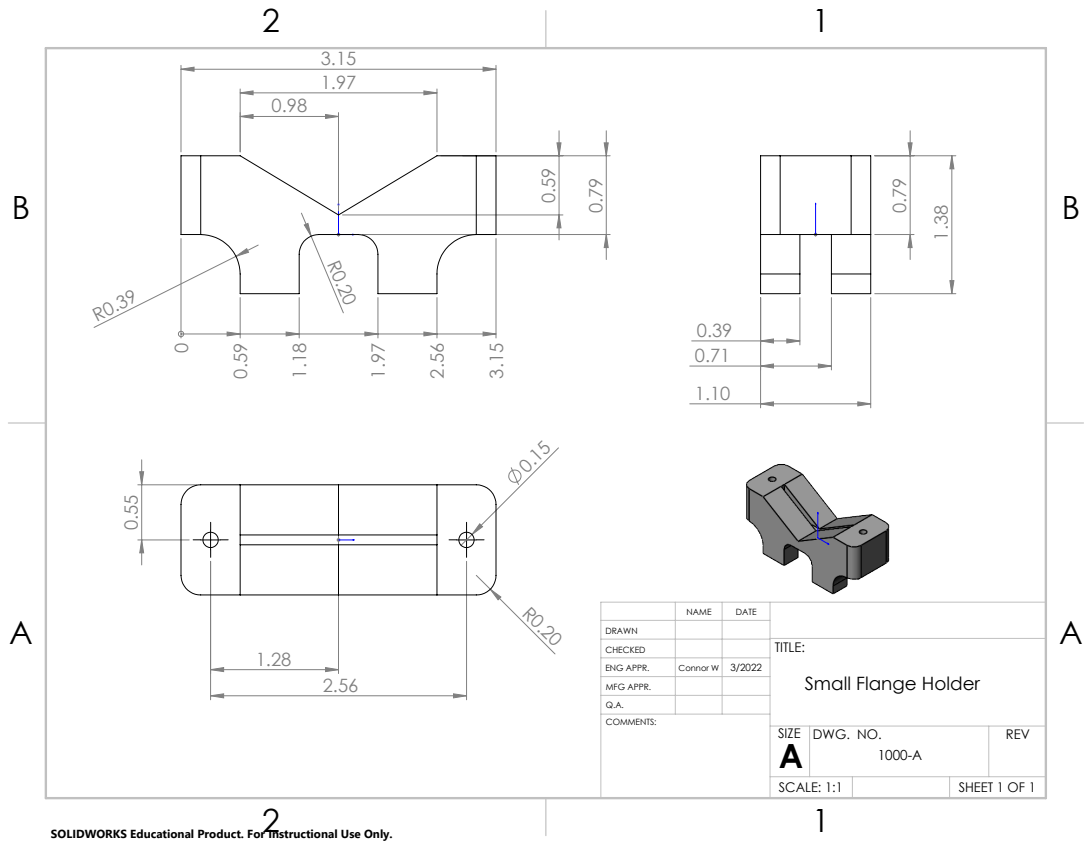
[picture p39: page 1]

NAME | DATE

DRAWN
CHECKED | | | TITLE: Small Flange Holder

ENG APPR. | Connor W | 3/2022
MFG APPR.
Q.A.

SIZE A | DWG. NO. 1000-A | REV

SCALE: 1:1 | | SHEET 1 OF 1

SOLIDWORKS Educational Product. For Instructional Use Only.

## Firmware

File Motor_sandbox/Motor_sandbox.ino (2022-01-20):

#include <TimerOne.h>         // Custom PWM freq
#include <Wire.h>             // I2C 


// Test Variables
#define MANUAL                // Comment to cancel manual mode
#define TESTING               // Comment to cancel testing
#define SERIAL_COMMS          // Comment to cancel serial comms
#define I2C_COMMS             // Comment to cancel I2C comms


// State machine 
enum State_enum {STANDBY, DATAPULL, CALC, RUN_S, RUN_J, STOP};           // States of the state machine
enum Signal_enum {ESTOP, START, JOG, BACK};                     // signals for traversing 
unsigned int state = STANDBY;                                   // default state 
bool TICKET = false;                                            // Confirmation to run the motor after data RX
bool FINISH = false;                                            // User def duration has been reached
 

// Pin Connections
#define STEP 9                // PWM signal for motor
#define DIR 6                 // Direction of motor
#define STBY 2                // Controller's standby enable (both EN and STBY must be low for low power mode)
#define M1 7                  // microstep config bit 1
#define M2 8                  // microstep config bit 2
// NOTE : STEP, DIR, M2, M1 are all used to set the microstep in the init latching 
//        but only STEP and DIR are availible after init


// Common States
#define FORWARD LOW           // motor direction
#define REVERSE HIGH          // motor direction


// Microstep settings  [ M1, M2, STEP, DIR ]
#define S_FULL  0x0
#define S_HALF  0xA
#define S_QRTR  0x5
#define S_8     0xE
#define S_16    0xF
#define S_32    0x4
#define S_64    0xD
#define S_128   0x8
#define S_256   0x6
char step_config = S_FULL;          // Set default to full step


// Pulse/Freq Variables
#define DC  0.5 * 1024              // Duty Cycle of PWM
#define MTR_FREQ_MAX 681            // Max freq motor can handle [Hz]
#define MTR_FREQ_MIN 120            // Min freq " 


// Physical Variables
#define INTERNAL_STEP 200           // Internal step size of the motor
#define GEAR_RATIO  99.05           // gear ratio of the planetary gear
#define THREAD_PITCH  0.005         // thread pitch of the actuator's screw [m]
float syr_radius_user = 0.010845;   // RADIUS of the 30ml BD syringe [m]
float q_user = 0.00001;             // volumetric flow rate as requested by user [L/s]
float freq = 200;                   // [sec/step]
unsigned int sec_user = 0;          // User requested sec duration
unsigned int min_user = 0;          // User requested min duration
unsigned int hour_user = 0;         // User "         hour "






void setup() {

  Serial.begin(9600);                           // Serial comms init

  //I2C comms setup

  pinMode(STEP, OUTPUT);                        // Setup controller pins
  pinMode(DIR, OUTPUT);
  pinMode(STBY, OUTPUT);
  pinMode(M1, OUTPUT);
  pinMode(M2, OUTPUT);
  digitalWrite(DIR, REVERSE);                   // Direction of motor

  
  init_control(step_config);                    // init controller
  delay(10);

      #ifdef MANUAL
      //q_user = 0.00000006944444444;             // Manually set the Q from code 
      q_user = 0.00001;
      #endif

  freq =  Q_to_Freq(q_user, syr_radius_user);     // Get period from Q

      #ifdef TESTING
      Serial.println(freq,8);
      #endif
    
  
  Timer1.initialize((1/freq) * 1000000);          // Init custom PWM freq[microsec] (mult to conv to usec)

      #ifdef MANUAL
      Timer1.pwm(STEP, DC);                  // Pulse the motor 
      #endif
    
}

void loop() {
}




/*~~~~~~~~~~~~~~~~~~~~~~~ init_config() ~~~~~~~~~~~~~~~~~~~~~~~~~~~~~~~~~~~~~~~~
 *  Purpose : initialize or change the md39a controllers step size
 *  Input : 0x4'b  [ M1, M2, STEP, DIR ] as calculated by the requested step setting
 *  Outut : 
 *  Notes : ~EN pin is held low 
 */
void init_control(char pin_config) {

  //The recommended power-up sequence is following:
  
  //1. Power-up the device applying the VS supply voltage but keeping both STBY and EN/FAULT inputs low.
  digitalWrite(STBY, LOW);
  
  //2. Set the MODEx inputs according to the target step resolution (see Table 1).
  digitalWrite(DIR, pin_config & 1);
  digitalWrite(STEP, (pin_config >> 1) & 1);
  digitalWrite(M2, (pin_config >> 2) & 1);
  digitalWrite(M1, (pin_config >> 3) & 1);
  
  //3. Wait for at least 1 µs (minimum tMODEsu time).
  delayMicroseconds(1);
  
  //4. Set the STBY high. The MODEx configuration is now latched inside the device.
  digitalWrite(STBY, HIGH);
  
  //5. Wait for at least 100 µs (minimum tMODEho time).
  delayMicroseconds(100);
  
  //6. Enable the power stage releasing the EN/FAULT input and start the operation.
}





/*~~~~~~~~~~~~~~~~~~~~~~~ Q_to_Freq() ~~~~~~~~~~~~~~~~~~~~~~~~~~~~~~~~~~~~~~~~
 *  Purpose : Convert the requested Q rate into a frequency for the stepper motor 
 *  Input : q_user, syr_radius, Physical quantities
 *  Outut : freq 
 */
float Q_to_Freq( float Q, float Radius){
  
  float freq = ( Q * INTERNAL_STEP * GEAR_RATIO) / (500 * Radius * Radius * THREAD_PITCH);
  return freq;
}





/*~~~~~~~~~~~~~~~~~~~~~~~~ MicroCali() ~~~~~~~~~~~~~~~~~~~~~~~~~~~~~~~~~~~~~~~~~~~~
 *  Purpose : Recalibrate the md39a motor controller's microstep setting to accomidate the min freq recommendation
 *            Max freq will result in Full step at max freq + warning
 *  Input : frequency, [global] step_config, [global] MTR_FREQ_MAX, [global] MTR_FREQ_MIN
 *  Output : frequency, [global] step_config
 *  Notes : Removes decimal point to save memory
 */
double MicroCali( float frequency ){


  // If greater than the max frequency
  if ( frequency > MTR_FREQ_MAX){
    step_config = S_FULL;                                                 // Set controller to full step

        #ifdef MANUAL
        Serial.println(" Requested Q value exceeds hardware's MAX RPS");  // Inform user
        #endif
        
    return MTR_FREQ_MAX;                                                  // Set freq to max
  }

  // Or if less than the min freq
  else if (frequency < MTR_FREQ_MIN){
    
    double microstep = MTR_FREQ_MIN / frequency;                 // Microstep size 
    
    if ( microstep <= 2 ){                                                // Half step
      step_config = S_HALF;                                               // Set controller to half step
      return 2 * frequency;                                               // double freq
    }

    else if ( microstep <= 4 ){
      step_config = S_QRTR;                                               // Set controller to half step
      return 4 * frequency;                                               // double freq
    }

    else if ( microstep <= 8 ){
      step_config = S_8;                                               
      return 8 * frequency;                                               
    }

    else if ( microstep <= 16 ){
      step_config = S_16;                                               
      return 16 * frequency;                                               
    }

    else if ( microstep <= 32 ){
      step_config = S_32;                                               
      return 32 * frequency;                                               
    }

    else if ( microstep <= 64 ){
      step_config = S_64;                                               
      return 64 * frequency;                                               
    }

    else if ( microstep <= 128 ){
      step_config = S_128;                                              
      return 128 * frequency;                                              
    }

    else if ( microstep <= 256 ){
      step_config = S_256;                                              
      return 256 * frequency;                                             
    }

    else{
      step_config = S_256;                                                 // Set controller to smallest step

        #ifdef MANUAL
        Serial.println(" Requested Q value is below hardware's MIN RPS");  // Inform user
        #endif
        
    return MTR_FREQ_MIN;                                                  // Set freq to min
      
    }
 }

 // No microstepping change needed
 else{
  return frequency;
 }
   
}




/* ~~~~~~~~~~~~~~~~~~~~~~~~ state_machine() ~~~~~~~~~~~~~~~~~~~~~~~~~~~~~~~~~~~~~~~~~~
 *  Purpose : Control the flow of the motor controller 
 *  Input : User input signals
 *  Output : 
 */

 void state_machine(uint8_t signals){
  
  switch(state){
    
    case STANDBY:
        
        // Serial GUI

        // read serial/I2C

        //logic placement
        
        break;

    case DATAPULL:
        break;

    case CALC:
        break;

    case RUN_J:
        break;


    case RUN_S:
        break;

    case STOP:
        break;

    default:
        state = STOP;
        break;

    
  }
 }

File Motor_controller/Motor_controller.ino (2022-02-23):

// Connor Wilson
// Winter 2022
// SMSS Motor Controller V1.0

#include <TimerOne.h>           // Custom PWM freq (ONLY WORKS WITH MEGA328 - NO MICRO BOARDS) - PWM only for pins(9, 10) on nano
#include <Wire.h>               // I2C 



// Test Variables (COMMENT OUT TO DESELECT) -- DONT FORGET TO CHANGE ARD ADDRESS (i2c_address) BELOW
#define TESTING               // Comment to cancel testing
//#define SERIAL_COMMS          // Comment to cancel serial comms [manual testing]
#define I2C_COMMS               // Comment to cancel I2C comms
//#define STSPIN220             // Comment out to NOT use the STSPIN220 Pololu low-volt motor controller
#define STSPIN820             // Comment out to NOT use the STSPIN820 Pololu high-volt motor controller


// State machine 
enum State_enum {STANDBY, DATAPULL_S, DATAPULL_J, RUN_S, RUN_J, STOP};  // States of the state machine
unsigned int state = STANDBY;                                           // default state 
#define START 'S'
#define JOG 'J'
#define BACK 'B'
#define ESTOP 'E'
bool TICKET = false;        // true if user supplied data is valid with hardware
bool FINISH = false;        // true if user requested duration is matched by hardware 



#ifdef STSPIN220 // Low voltage motor controller library
    // Pin Connections 
    #define M1 2                  // microstep config bit 1
    #define M2 3                  // microstep config bit 2
    #define STBY 5                // Controller's standby enable (both EN and STBY must be low for low power mode)
    #define STEP 9                // PWM signal for motor
    #define DIR 7                 // Direction of motor
    // NOTE : STEP, DIR, M2, M1 are all used to set the microstep in the init latching 
    //        but only STEP and DIR are availible after init
  
  
    // LED State Indicators
    #define YELLOW 8
    #define BLUE 10
    #define WHITE 11 
    #define GREEN 12



        // Microstep settings for md39a[ M1, M2, STEP, DIR ]
    #define S_FULL  0x0
    #define S_HALF  0xA
    #define S_QRTR  0x5
    #define S_8     0xE
    #define S_16    0xF
    #define S_32    0x4
    #define S_64    0xD
    #define S_128   0x8
    #define S_256   0x6
    char step_config = S_FULL;                  // Set default to full step
#endif


#ifdef STSPIN820 // High voltage motor controller library
    // Pin Connections 
    #define M1 2                  // microstep config bit 1
    #define M2 3                  // microstep config bit 2
    #define M3 4                  // microstep config bit 3
    #define STBY 5                // Controller's standby enable (both EN and STBY must be low for low power mode)
    #define STEP 9                // PWM signal for motor
    #define DIR 7                 // Direction of motor
    // NOTE : M1-3 are used for microstep latching (ie STEP/DIR are not used for latching like the STSPIN220)
  
  
    // LED State Indicators
    #define YELLOW 8
    #define BLUE 10
    #define WHITE 11 
    #define GREEN 12



        // Microstep settings for md39a[ M1, M2, STEP, DIR ]
    #define S_FULL  0x0
    #define S_HALF  0x4
    #define S_QRTR  0x2
    #define S_8     0x6
    #define S_16    0x1
    #define S_32    0x5
    //#define S_64  no 64 bit
    #define S_128   0x3
    #define S_256   0x7
    char step_config = S_FULL;                  // Set default to full step
#endif


// Motor States
#define FORWARD LOW           // motor direction for pin logic
#define REVERSE HIGH          // motor direction for pin logic
bool DIRECTION = FORWARD;     // motor direction
bool RUNNING  = false;        // true if motor is running





// Pulse/Freq Variables
#define DC  0.8 * 1024                      // Duty Cycle of PWM                                          [UNSURE WHAT RATIO IS BEST]
#define MTR_FREQ_MAX 875                    // Max freq motor can handle [Hz]
#define MTR_RES_MIN 120                     // Min freq for smooth performance [Hz]
#define MTR_FREQ_MIN 0                      // Min freq motor can handle [Hz]                             [UNKNOWN]


// Physical Variables
#define INTERNAL_STEP 200                   // Internal step size of the motor
#define GEAR_RATIO  99.05                   // gear ratio of the planetary gear
#define THREAD_PITCH  0.005                 // thread pitch of the actuator's screw [m]
float syr_capacity = 30;                    // capacity of syringe in mL
float syr_radius_user = 11;                 // RADIUS of the 30ml BD syringe [m]
float q_user = 0;                           // volumetric flow rate as requested by user [L/s]
float freq = 200;                           // [sec/step]
unsigned long sec_user = 0;                 // User requested sec duration
unsigned long min_user = 0;                 // User requested min duration
unsigned long hour_user = 0;                // User "         hour "
unsigned long duration = 0;                 // Run time {msec}
unsigned long time_stamp_start = 0;         // time keeping 
unsigned long time_stamp_end = 0;           // "


// Serial Variables
#ifdef SERIAL_COMMS
    char receivedChar;                          // pool for char data
    boolean newData_char = false;               // true if new char data is RX 
    boolean newData_str = false;                // true if new str data is RX 
    const byte numChars = 32;                   // str length when TX 
    char receivedChars[numChars];               // pool for str data 
    bool displayed = false;                     // true if graphic is displayed 
#endif
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

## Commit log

2022-01-16 Arduino Dir Housing
2022-01-20 Added a semi-working serial arduino controller
2022-01-21 Tuts 1 and 2 (printing, colors, and text attributes)
2022-01-22 Debugging Ver1.1
    1) Duration unsigned int problem
    2) Added LED markers for each state
    3) Fixed DATAPULL_J radius variable
    4) Added some debugging serial text
2022-01-25 Fixed init_controller placement and removed red LED
2022-01-26 Fixed FWD/BCK motor overwrite and removed the time tests
2022-01-27 Wire library outline for Pi
2022-01-28 Functioning : basic call and respond from Pi to arduino
2022-02-01 Added frame of GUI
2022-02-02 Added different pinout for arduino micro
2022-02-04 I2C can change state of arduino now... unsure about float blocks through I2C though
2022-02-10 Have working back end but need to redo estop : I dont want polling but rather a moving estop button with the option to estop all
    Time delay in reporting is between 1.3 sec between each device and near 4 sec betwen looping
    I would want to poll for time in larger intervals to get better estop response times
    This code has yet to loop back to START naturally
    end case is not triggering fully with last device (might has missed the window to send FINISH)
    Considering speeding up the I2c rate but unsure
    100ms delay per TX and 4 TX per data signal -> +400ms per variable
2022-02-11 Fixed: Time / Finish flags Added adddress related delay to that the ards can start at the same time
    Still at large
    Some user errors are not triggering
    All-estop has each device turn off in a random order....
2022-02-17 small bug with DIR motor direction
2022-02-23 Fixed error with motor direction
    Added STSPIN820 controller option and redesigned the existing (md39a) STSPIN220 pinout
    so that they are interchangable
2022-03-11 Adding latest parts
    [BallScrewGuide.SLDPRT, BallScrewGuide.STL, PillowBlock.SLDPRT, Small_Finger_Flange_holder.SLDDRW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]
